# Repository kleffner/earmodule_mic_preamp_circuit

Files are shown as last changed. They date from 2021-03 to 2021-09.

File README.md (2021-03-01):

# Ear Module Mic Pre-Amp Circuit
* Author: Matt Kleffner
* License: CC BY-SA 4.0 or Later

# Requirements:
* Interface hearing-aid mems microphones to sound card
* Low power
* Low noise, less than or equal to EIN of mic
* High-impedance interface
  * Mic output impedance on the order of 5 kOhm
* 100 Ohm output to drive high-impendance sound cards
* Single-ended input
* Differential output
* 1V Mic-bias supply needed
* Bi-polar AA power supply, +/- 3.2V, operate down to +/- 2V
* Op-amps provide clean 3.5V swing at +/- 2V supply

# Filter Gain Requirements
* Typical mic sensitivity is -38 dB re 1V/Pa or approx. 0.0125 V/Pa
* 120 dB is 20 Pa (10^(120/20)*20e-6)
* Mic output voltage at 120 dB is 20 Pa * 0.0125 V/Pa = 250 mV
* Gain for 120 V -> 3.5 V is 3.5/.250 = 14
* Allow for overshoot and set gain to 7
* Set input impedance to 20K, which is feedback impedance of 140K
  * Higher input impedances could increase circuit noise
* Mic output voltage will be scaled to approx 20/(20+5) or 20% reduction
* Match resistance seen on both + and - terminals
* 20K//140K = 17.5K - not available, but lots of 17.4K and 100 are

# Filter Cutoff Requirements
* Cost-effective, tight tolerances are 0.1% resistors, 5% capacitors
* Low cutoff < 20Hz, including tolerances
  * R = 20K, C=0.47e-6 gives (min,nom,max) cutoff of (16.1, 16.9, 17.8) Hz
* High cutoff > 20kHz, including tolerances
  * R = 140K, C=51pF gives (min,nom,max) cutoff of (21.2, 22.3, 2.35) kHz

# Op-amp selection
* Input stage
  * Implements filter
  * Low-noise
  * Low output impedance
  * Candidates
    * ADA4807
    * ADA4177
    * ADA4661 seems to be the best selection for the constraints

* Differential output stage
  * Requirements:
  * Unity-gain
  * Single-to-differential operation
  * Built-in over-voltage protection
  * Low-noise
  * Accurate differential-input impedance
  * Use ADA8476
    * Matched to <0.05% error
    * Protection to over 18V 

# Voltage regulator
* Low-noise
* Low component count
* TPS7A2010 Looks good but doesn't seem available in desired package
* TLV71210 is close, use it

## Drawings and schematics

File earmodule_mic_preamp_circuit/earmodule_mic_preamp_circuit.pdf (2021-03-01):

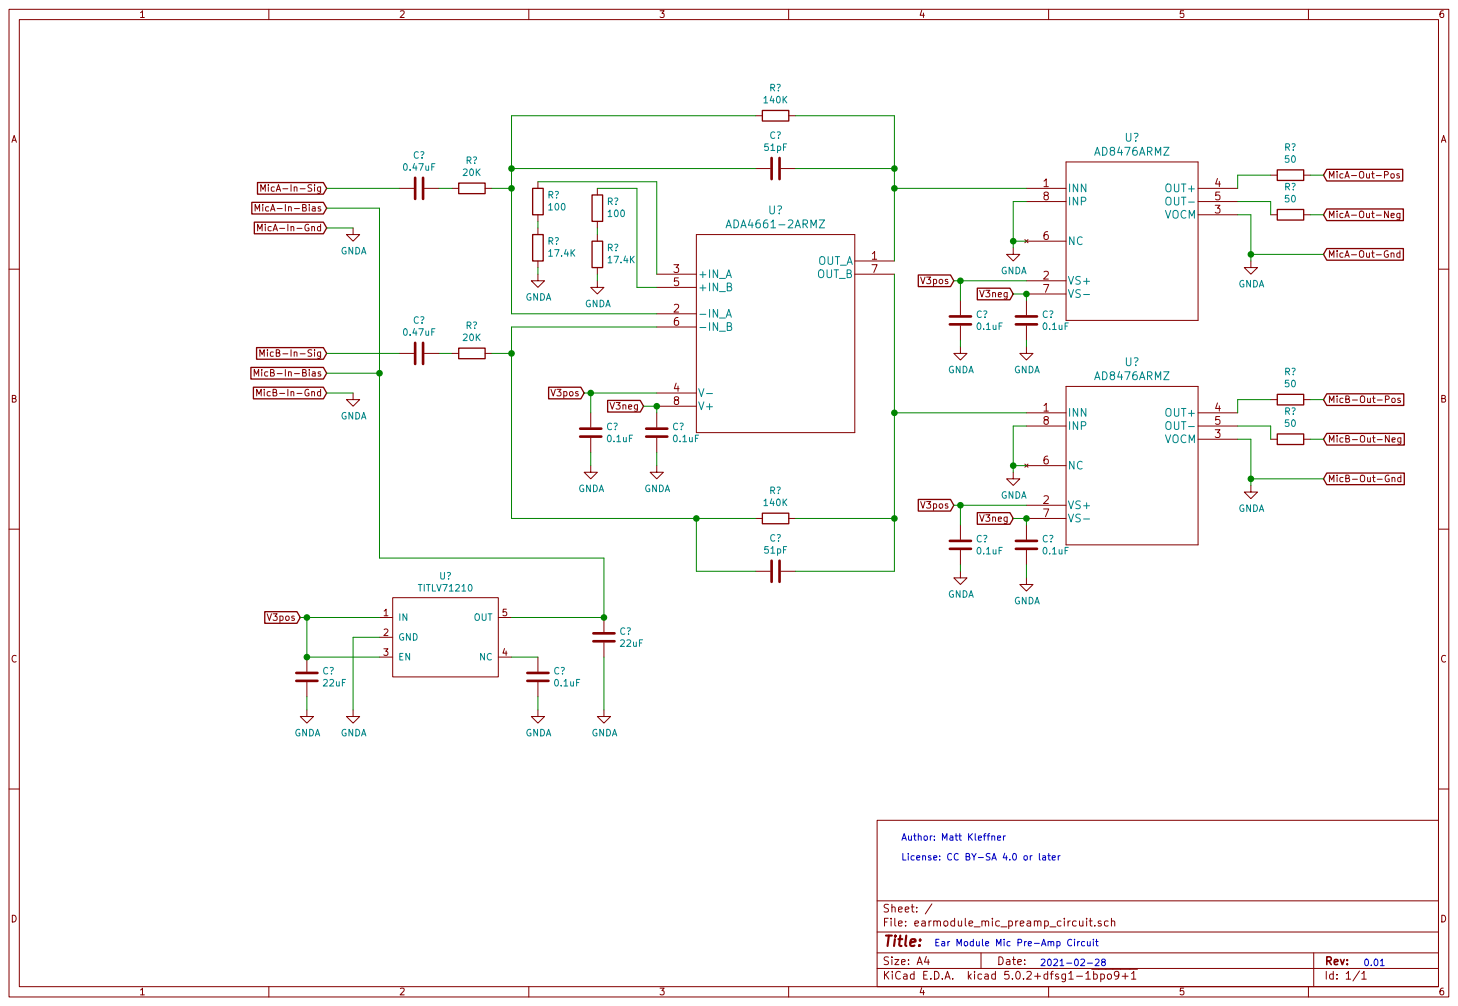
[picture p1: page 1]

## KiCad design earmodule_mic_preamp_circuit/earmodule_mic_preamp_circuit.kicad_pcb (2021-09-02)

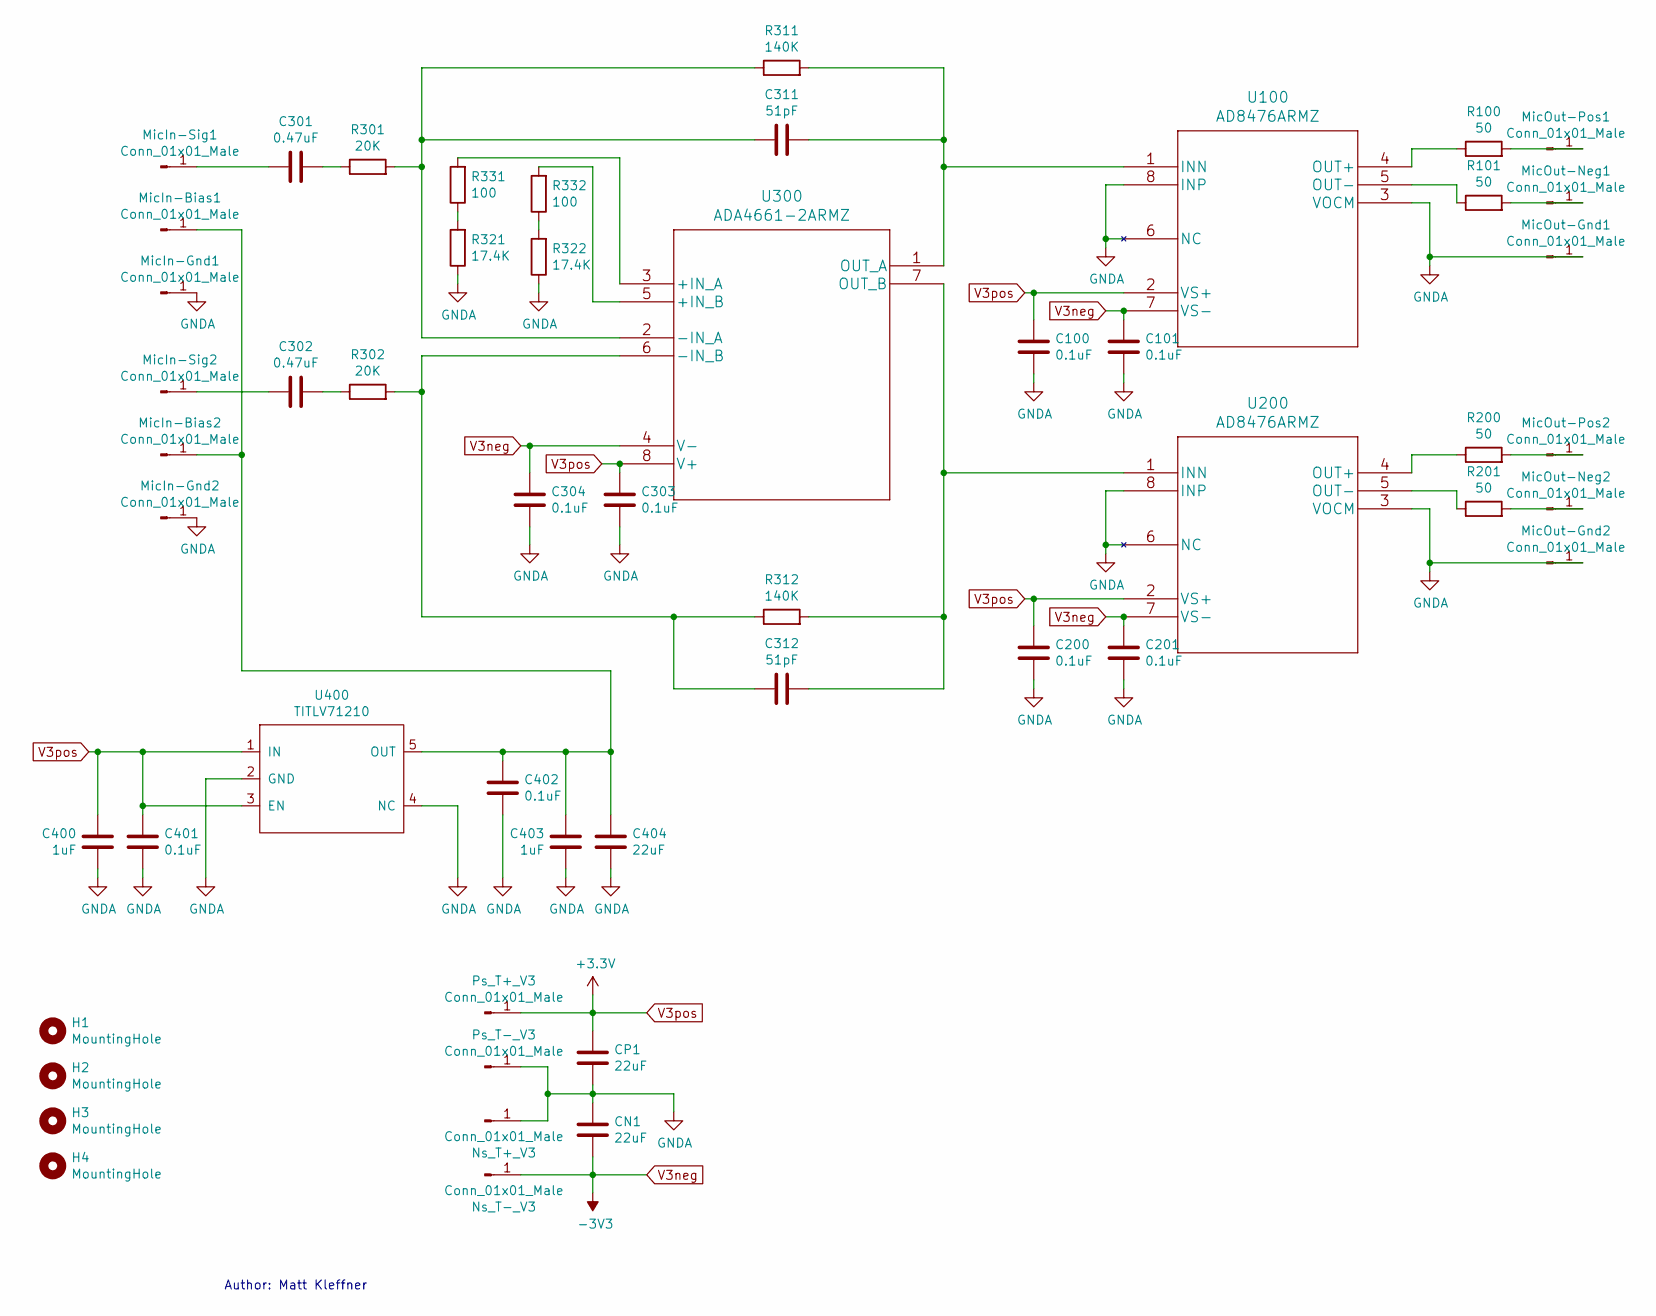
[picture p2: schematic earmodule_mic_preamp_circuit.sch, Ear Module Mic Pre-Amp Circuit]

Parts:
C100, C101, C200, C201, C303, C304, C401, C402: 0.1uF; C_0402_1005Metric
C301, C302: 0.47uF; C_0402_1005Metric
C311, C312: 51pF; C_0402_1005Metric
C400, C403: 1uF; C_0805_2012Metric_Pad1.15x1.40mm_HandSolder
C404: 22uF; C_1206_3216Metric_Pad1.42x1.75mm_HandSolder
CN1: 22uF; C_1206_3216Metric_Pad1.42x1.75mm_HandSolder
CP1: 22uF; C_1206_3216Metric_Pad1.42x1.75mm_HandSolder
H1, H2, H3, H4: MountingHole; MountingHole_2.7mm_M2.5_ISO7380
MicIn-Bias1, MicIn-Bias2: Conn_01x01_Male; TestPoint_Pad_D4.0mm
MicIn-Gnd1, MicIn-Gnd2: Conn_01x01_Male; TestPoint_Pad_D4.0mm
MicIn-Sig1, MicIn-Sig2: Conn_01x01_Male; TestPoint_Pad_D4.0mm
MicOut-Gnd1, MicOut-Gnd2: Conn_01x01_Male; TestPoint_Pad_D4.0mm
MicOut-Neg1, MicOut-Neg2: Conn_01x01_Male; TestPoint_Pad_D4.0mm
MicOut-Pos1, MicOut-Pos2: Conn_01x01_Male; TestPoint_Pad_D4.0mm
Ns_T+_V3: Conn_01x01_Male; TestPoint_Pad_D4.0mm
Ns_T-_V3: Conn_01x01_Male; TestPoint_Pad_D4.0mm
Ps_T+_V3: Conn_01x01_Male; TestPoint_Pad_D4.0mm
Ps_T-_V3: Conn_01x01_Male; TestPoint_Pad_D4.0mm
R100, R101, R200, R201: 50; R_0402_1005Metric
R301, R302: 20K; R_0402_1005Metric
R311, R312: 140K; R_0402_1005Metric
R321, R322: 17.4K; R_0402_1005Metric
R331, R332: 100; R_0402_1005Metric
U100, U200: AD8476ARMZ
U300: ADA4661-2ARMZ
U400: TITLV71210; SOT-23-5_HandSoldering

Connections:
GNDA: C100.2, C101.2, C200.2, C201.2, C303.2, C304.2, C400.2, C401.2, C402.2, C403.2, C404.2, CN1.1, CP1.2, MicIn-Gnd1.1, MicIn-Gnd2.1, MicOut-Gnd1.1, MicOut-Gnd2.1, Ns_T+_V3.1, Ps_T-_V3.1, R321.1, R322.1, U100.3 (VOCM), U100.6 (NC), U100.8 (INP), U200.3 (VOCM), U200.6 (NC), U200.8 (INP), U400.2 (GND), U400.4 (NC)
unnamed: C301.1, R301.1
unnamed: C301.2, MicIn-Sig1.1
unnamed: C302.1, R302.1
unnamed: C302.2, MicIn-Sig2.1
unnamed: C311.1, R311.2, U100.1 (INN), U300.1 (OUT_A)
unnamed: C311.2, R301.2, R311.1, U300.2 (-IN_A)
unnamed: C312.1, R312.2, U200.1 (INN), U300.7 (OUT_B)
unnamed: C312.2, R302.2, R312.1, U300.6 (-IN_B)
unnamed: C402.1, C403.1, C404.1, MicIn-Bias1.1, MicIn-Bias2.1, U400.5 (OUT)
unnamed: MicOut-Neg1.1, R101.2
unnamed: MicOut-Neg2.1, R201.2
unnamed: MicOut-Pos1.1, R100.2
unnamed: MicOut-Pos2.1, R200.2
unnamed: R100.1, U100.4 (OUT+)
unnamed: R101.1, U100.5 (OUT-)
unnamed: R200.1, U200.4 (OUT+)
unnamed: R201.1, U200.5 (OUT-)
unnamed: R321.2, R331.1
unnamed: R322.2, R332.1
unnamed: R331.2, U300.3 (+IN_A)
unnamed: R332.2, U300.5 (+IN_B)
V3neg: C101.1, C201.1, C304.1, CN1.2, Ns_T-_V3.1, U100.7 (VS-), U200.7 (VS-), U300.4 (V-)
V3pos: C100.1, C200.1, C303.1, C400.1, C401.1, CP1.1, Ps_T+_V3.1, U100.2 (VS+), U200.2 (VS+), U300.8 (V+), U400.1 (IN), U400.3 (EN)

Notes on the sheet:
Author: Matt Kleffner

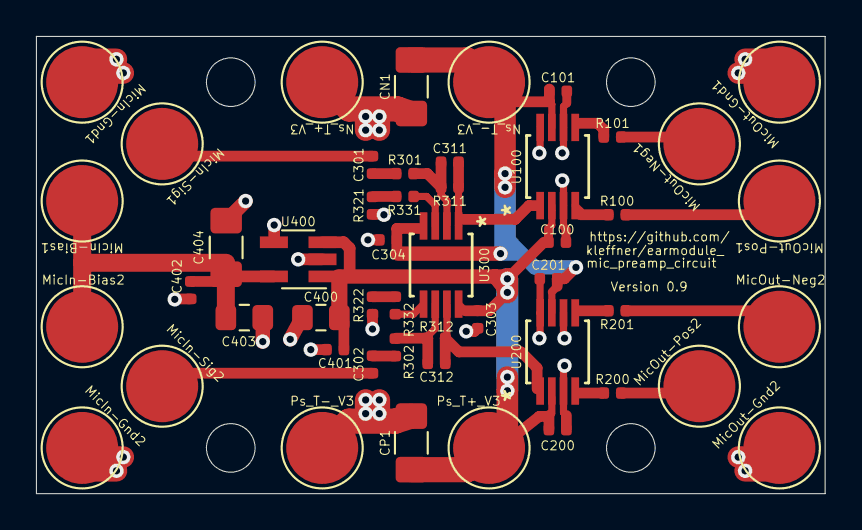
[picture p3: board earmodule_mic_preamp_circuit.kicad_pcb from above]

Board: 2 copper layers, 43.8 x 25.4 mm, 53 parts (0 on the bottom side), 24 nets.

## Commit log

2021-03-01 Initial circuit design and schematic capture
    [earmodule_mic_preamp_circuit.kicad_pcb, earmodule_mic_preamp_circuit.sch]
2021-08-17 First complete PCB layout. Silkscreen needs to be fixed.
    [earmodule_mic_preamp_circuit.kicad_pcb, earmodule_mic_preamp_circuit.sch]
2021-08-18 Shrink and position silkscreen
    [earmodule_mic_preamp_circuit.kicad_pcb]
2021-08-26 Rearranged regulator layout for better co-location of parts. Cleaned up interface names.
    [earmodule_mic_preamp_circuit.kicad_pcb, earmodule_mic_preamp_circuit.sch]
2021-09-01 Enlarged board and wire solder pad sizes. Added small decoupling caps in bias circuit. Finalized naming, numbering, and placement of text.
    [earmodule_mic_preamp_circuit.kicad_pcb, earmodule_mic_preamp_circuit.sch]
2021-09-02 Corrected miminum solder mask width. Aligned traces and copper fill along board edge to statisfy minimums. Removed backup file from repo.
    [earmodule_mic_preamp_circuit.kicad_pcb]

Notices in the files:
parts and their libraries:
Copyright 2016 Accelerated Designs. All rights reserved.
